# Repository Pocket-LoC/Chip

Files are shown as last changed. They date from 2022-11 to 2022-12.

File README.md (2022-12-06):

# Pocket LoC
 
Lab-on-chip (LoC) technology is becoming increasingly relevant, especially in the field of medicine. However, often LoC setups rely on complex lab equipment for operation. The aim of this project is to create an affordable and portable LoC setup as a proof-of-concept for truly pocket-sized LoC - the Pocket LoC.

Pocket LoC can be assembled with standard equipment found in a typical engineering lab (such as a maker space or FabLab). Once assembled, Pocket LoC is fully portable and only needs a PC to operate.

## Microfluidic Chip


This repository contains instructions and templates for making your own microfluidic chip. Principally, Pocket LoC can work with any transparent chip that fits the sensor dimensions. However, we would like to provide some guidance on how to get started.

### Materials
The microfluidic chips described here consist of PDMS (i.e. silicone) on a glass substrate. The necessary moulds are 3D-printed.

You will need the following components and tools:
- 3D-printer
- printing filament (we achieved best results with ABS or PETG, e.g. [black PETG](https://www.prusa3d.com/product/prusament-petg-jet-black-1kg/))
- silicone elastomer (many materials may work, we use [Sylgard 184](https://www.dow.com/en-us/pdp.sylgard-184-silicone-elastomer-kit.01064291z.html#overview))
- microscope slides as substrate
- vacuum chamber and pump (or a lab with vacuum supply)
- fine scales for mixing the silicone
- heat plate (optional)

### Design
The design of your microfluidic chip will depend on your individual application. If you just want to try the Pocket LoC with a simple droplet experiment we suggest using a large channel width of 1mm, that does not require any specific precision when manufacturing the chip. Have a look at the sampple mould.

Inlets can be designed as a press-fit for the [tubing]((https://darwin-microfluidics.com/collections/silicone-tygon-tubing/products/mp-t-1-3-mm-tygon-tubing-for-bartels-micropumps)) used for the Pocket LoC. The same applies for outlets.

Your channel structure should have a straight section, paralell to the chips long side, with a length of at least 6mm to use the Pocket LoC sensor. You may also have to print custom position holders (see the [housing repository](https://github.com/Pocket-LoC/Housing/tree/main/CAD) for some samples) to fit your channel structure.

### Manufacture
These instructons refer to Sylgard 184 elastomer. If you are using different silicone, start with the mixing and curing parameters suggested by the manufacturer and adjust the mix ration and curing time depending on your results.

1. Design and print your chip mould and a rake (used in step 6). Usually it is a good idea to make a few chips at once, as some may fail. Samples for both the rake and the chip are provided - you may have to adjust the size of the teeth of the rake depening on your printer and channel structure.
      <p float="left">
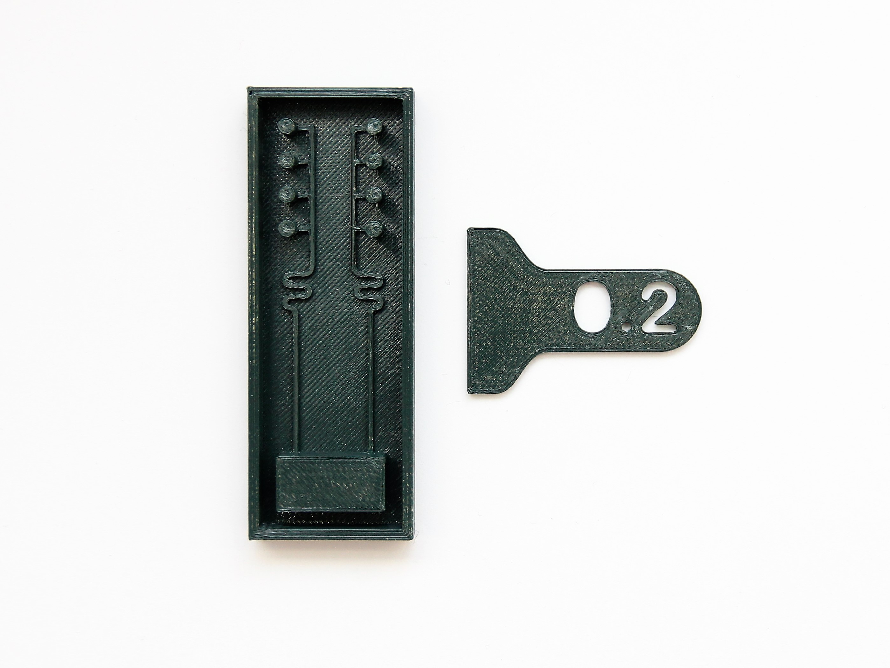
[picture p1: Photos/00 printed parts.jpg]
        
      </p>
2. Pour together the two components of the silicone kit using fine scales to get a ratio of 1:10. Typically, about 15g of mixture is a sufficient amount for one microfluidic chip. Mix the components well using a spoon or spatula for at least two minutes.
      <p float="left">
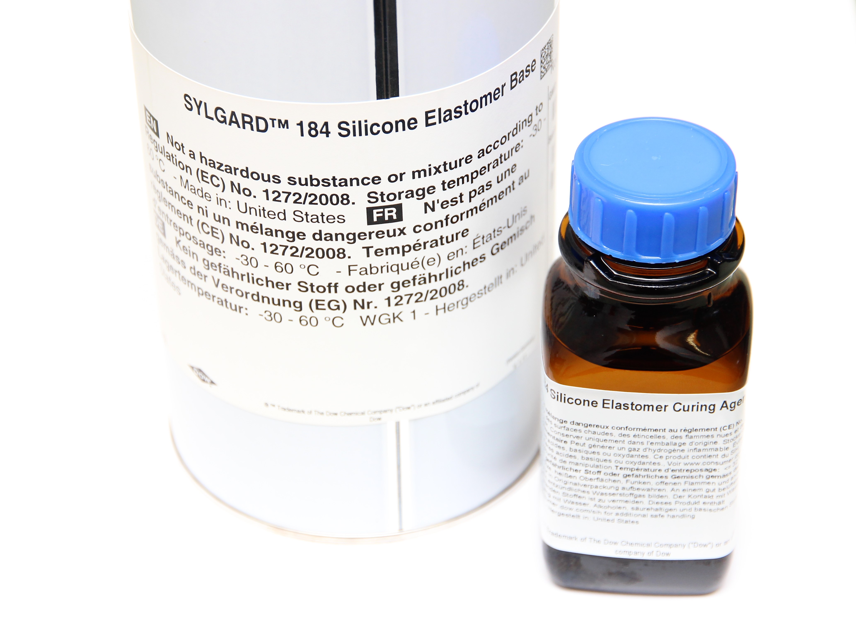
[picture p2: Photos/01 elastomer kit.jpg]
        
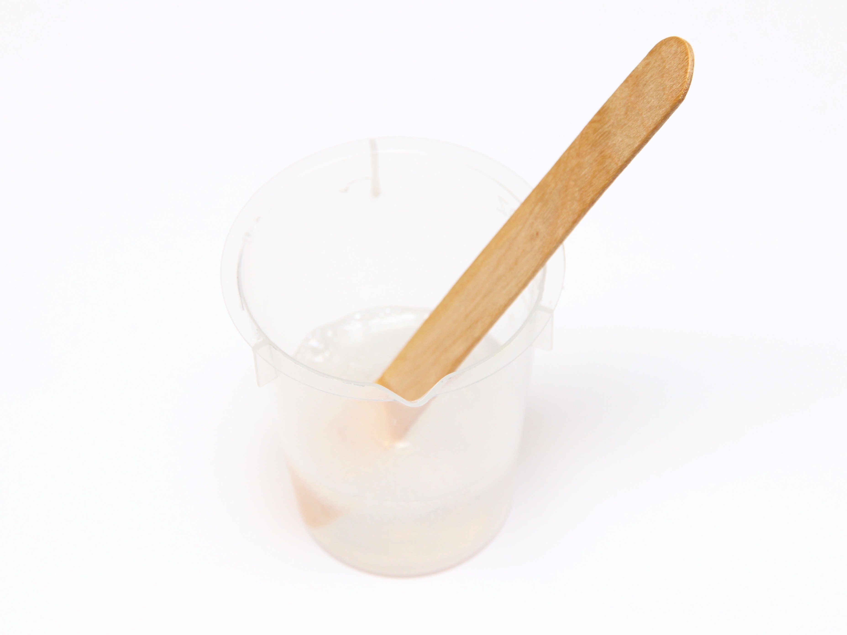
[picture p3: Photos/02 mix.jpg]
        
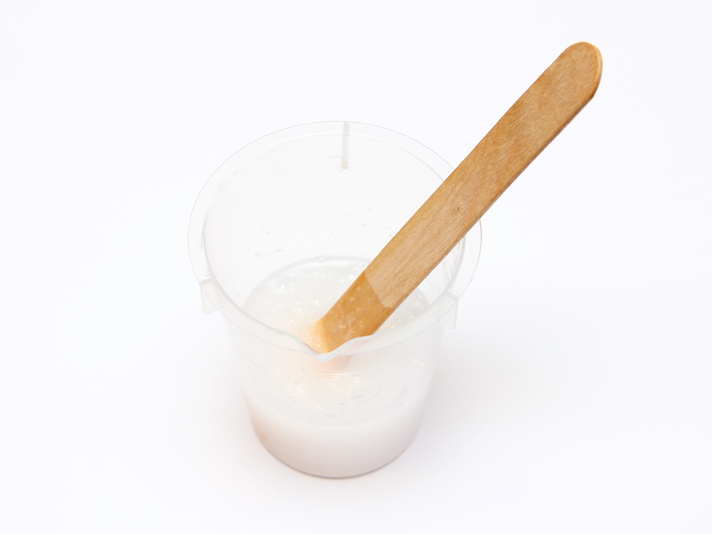
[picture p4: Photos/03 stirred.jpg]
        
      </p>

3. Place the silicone mixture in the vacuum chamber and evacuate the air to remove bubbles from the mixture. Wait for at least two minutes before ventilating the chamber again. Repeat approx. 10-20 times until all visible bubbles have been removed.
      <p float="left">
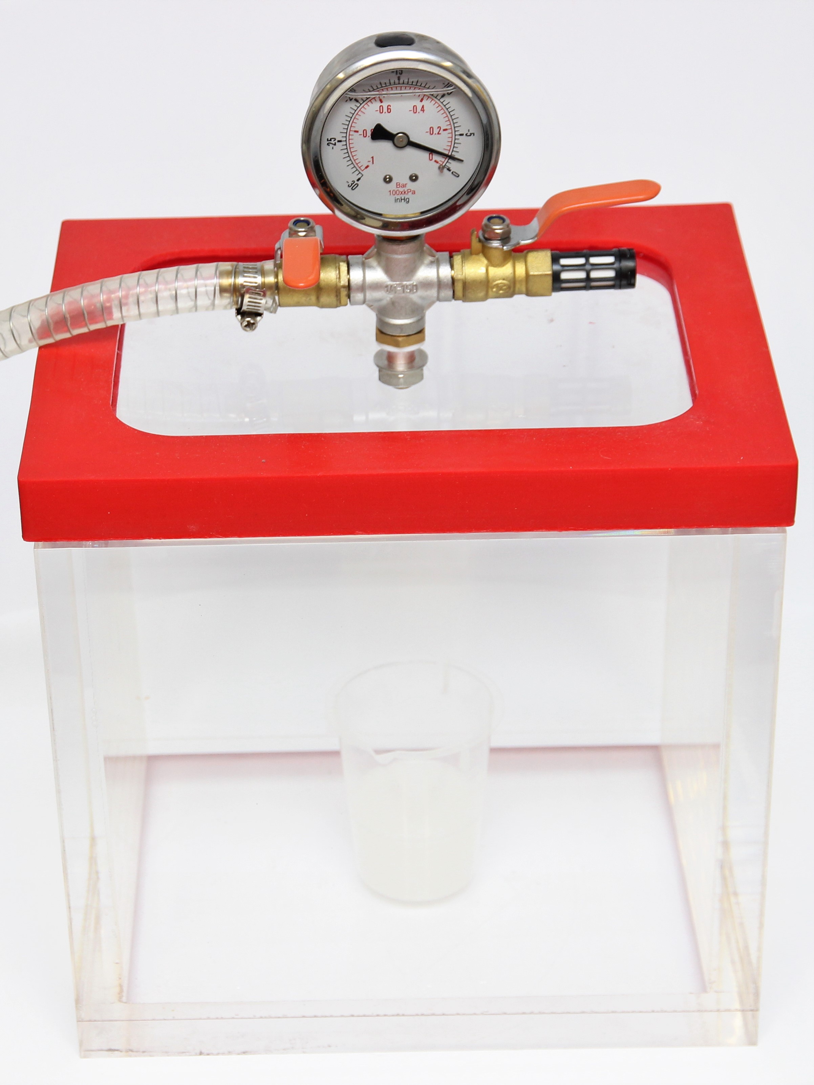
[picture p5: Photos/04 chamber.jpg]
        
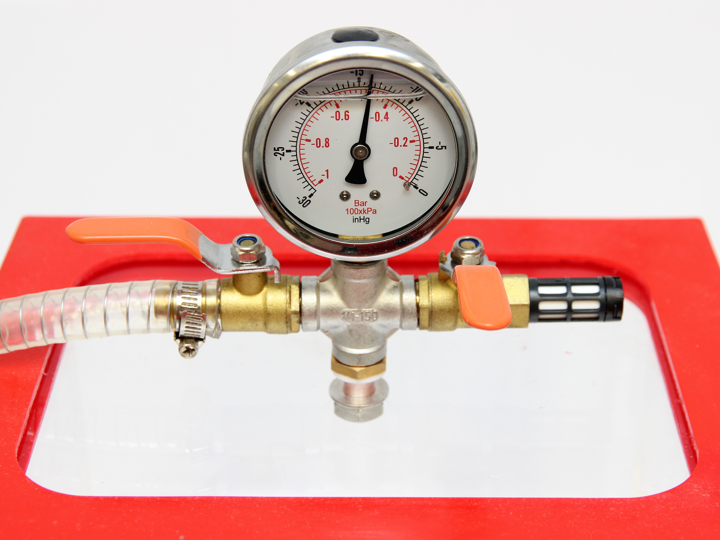
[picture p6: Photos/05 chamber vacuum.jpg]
        
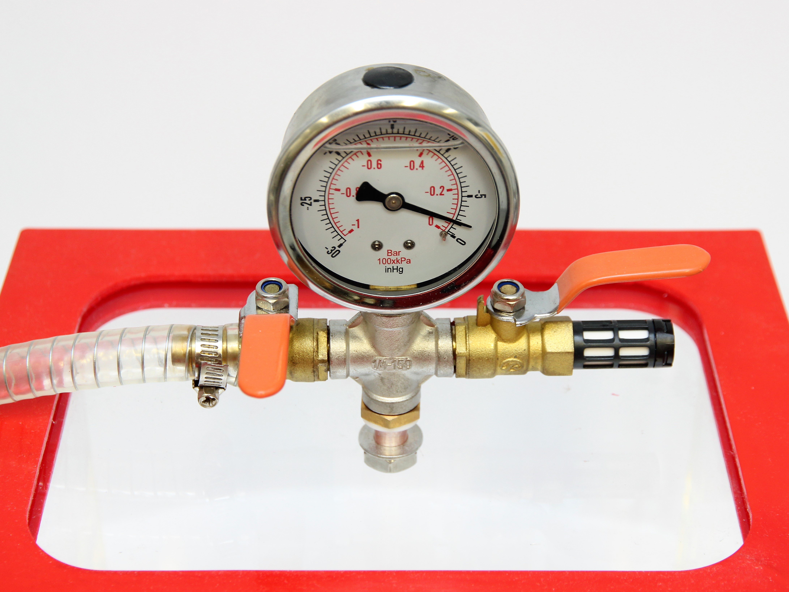
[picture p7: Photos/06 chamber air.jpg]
        
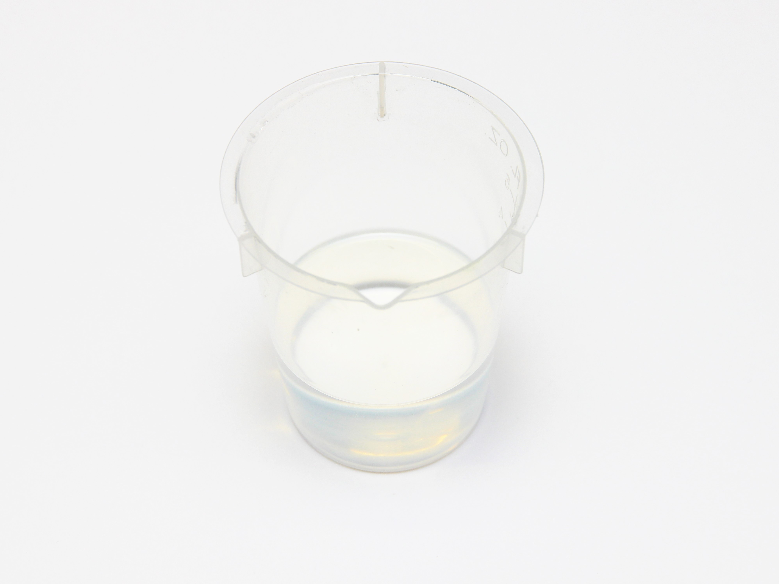
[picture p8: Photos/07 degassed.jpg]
        
      </p>

4. Pour the degassed silicone mixture into the mould, filling it to the brim. Then place it on a heat plate or in a lab oven to cure at 100°C for 60 minutes.
      <p float="left">
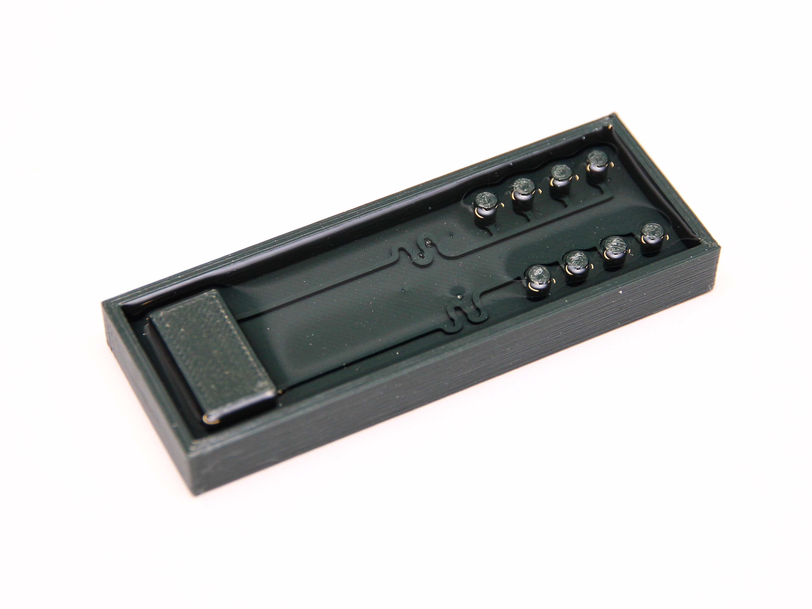
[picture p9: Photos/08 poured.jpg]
        
      </p>

5. Carefully pull the chip structure out of the mould. Start by lifting it at the edge with a thin screwdriver. You will see a fine grid caused by the 3D-print on the bottom of the chip. Remove any unwanted silicone residue. Depending on your chip structure and size it may be easier to break apart the mould.
      <p float="left">
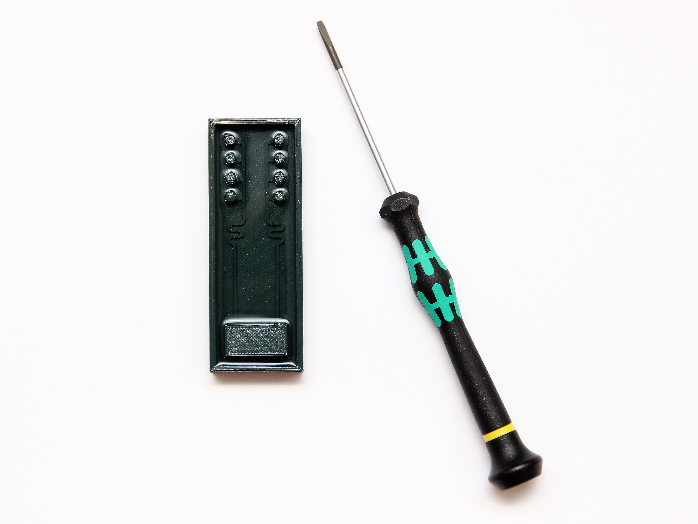
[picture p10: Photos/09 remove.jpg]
        
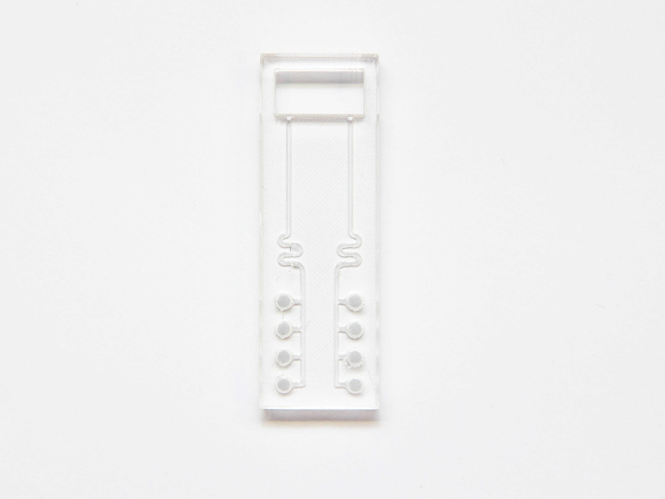
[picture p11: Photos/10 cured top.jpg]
        
      </p>

6. Use the rake to spread a thin and consistent layer of silicone on a clean microscope slide. Then carefully place the cured silicone chip on top and press lightly. You can use the grid structure as a visual aid: Ideally, it should only just not be visible any more. Adjust the size of the rake if the layer is too thin (chip will not attach properly) or too thick (your chip will be clogged once cured).
      <p float="left">
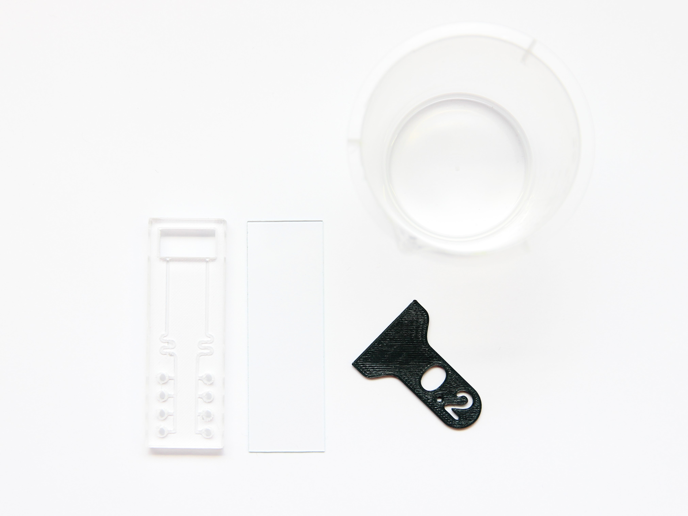
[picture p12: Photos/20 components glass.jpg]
        
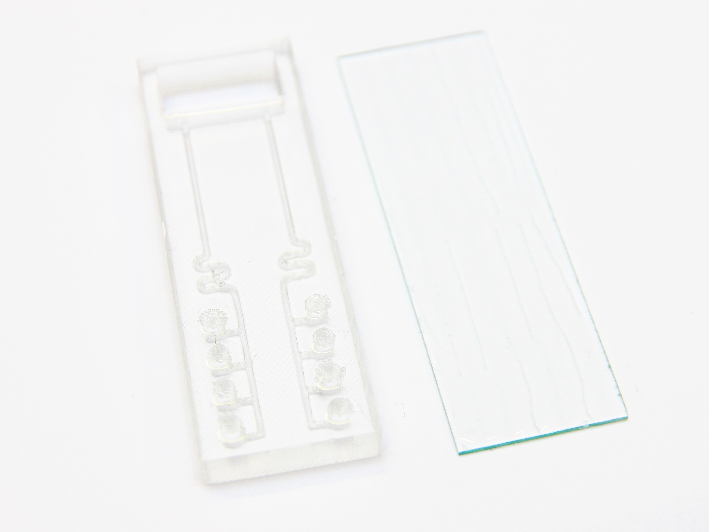
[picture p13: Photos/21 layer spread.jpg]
        
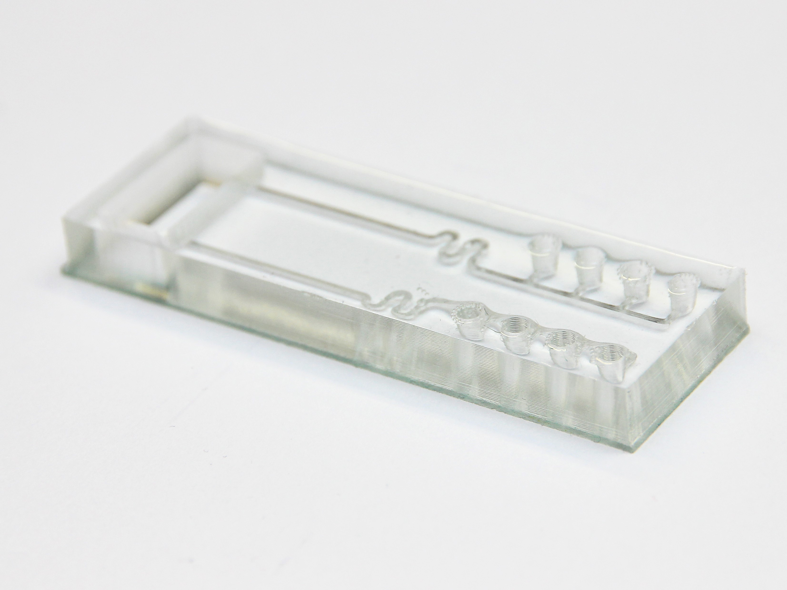
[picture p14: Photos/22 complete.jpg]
        
      </p>

7. Cure the chip for another 60 minutes at 100°C.

8. Your microfluidic chip is now ready to go. You may find some fine tuning of the manufacturing procedure for your needs and tools may improve the chip performance (e.g. reproducibility of droplet generation or pressure tolerance).

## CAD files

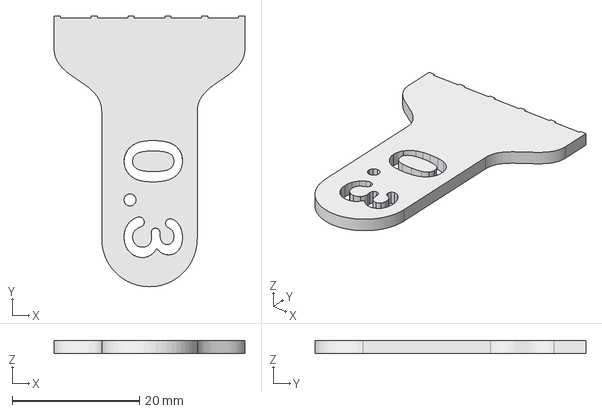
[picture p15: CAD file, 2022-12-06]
Rake.FCStd
30.0 x 42.5 x 2.00 mm

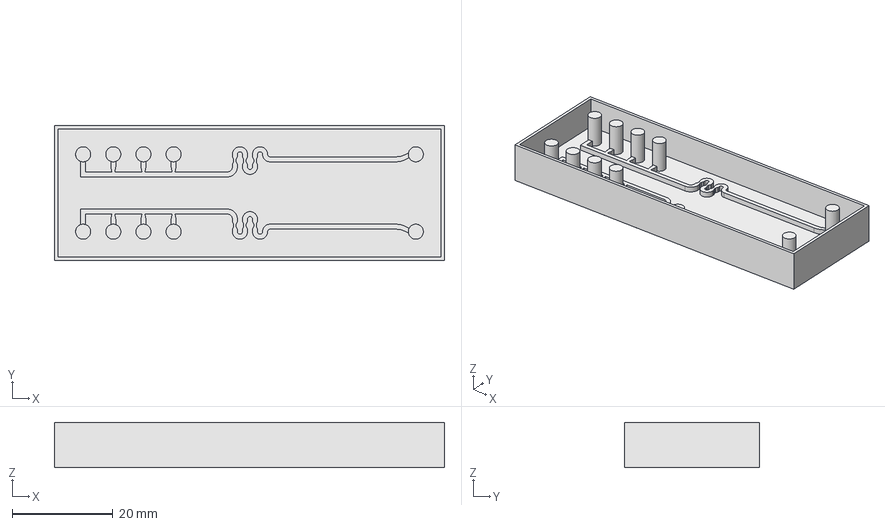
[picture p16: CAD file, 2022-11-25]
chip outlet tubes.FCStd
77.6 x 26.8 x 9.00 mm

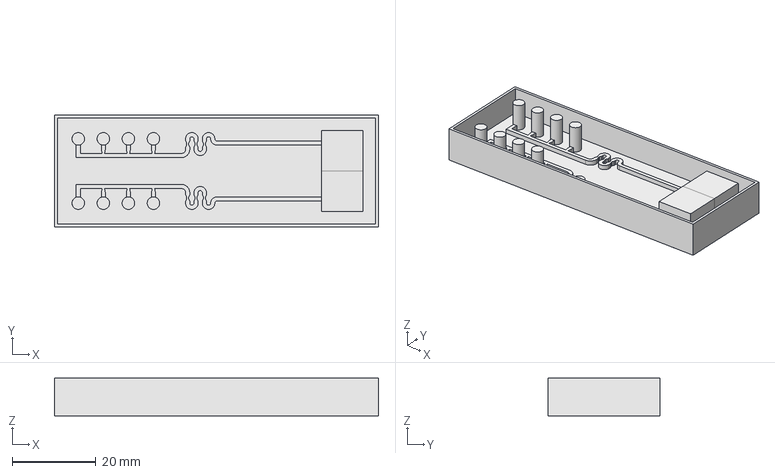
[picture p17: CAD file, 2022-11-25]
chip outlet basin.FCStd
77.6 x 26.8 x 9.00 mm

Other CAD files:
Rake.stl
chip outlet basin.stl
chip outlet tubes.stl

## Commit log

2022-11-22 Update chip samples
    [chip outlet basin.FCStd, chip outlet basin.stl, chip outlet tubes.FCStd, chip outlet tubes.stl]
2022-11-25 Thinner walls
    [Rake.FCStd, Rake.stl, chip outlet basin.FCStd, chip outlet basin.stl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]
2022-12-06 Update rake
    [Rake.FCStd, Rake.stl]
